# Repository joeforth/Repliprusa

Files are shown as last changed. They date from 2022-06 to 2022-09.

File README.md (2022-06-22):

# Repliprusa
Ongoing project to document modification of Prusa Mini+ 3D printer for Bioprinting. First stage of the process outlined in the conversion guide.
The project uses a modified version of the Feinberg group's Replistruder 4:

https://www.sciencedirect.com/science/article/pii/S2468067220300791

Contact j.forth@ucl.ac.uk if you need any help!

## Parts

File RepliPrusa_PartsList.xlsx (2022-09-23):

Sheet: Replistruder4
Core Parts | Link | Quantity Needed | Purchase Quantity | Detail | Cost
Prusa Mini+ | https://www.prusa3d.com/product/original-prusa-mini-semi-assembled-3d-printer-4/ | 1 | 1 | . | 339 | each
Printhead Conversion | Link | Quantity Needed | Purchase Quantity | Detail | Cost
M8 x 1.25 mm, 150 mm long Fully Threaded Hex Bolt | https://www.ebay.co.uk/itm/383694435663?var=652094637270 | 1 | 3 | . | 1.99 | each
M8 Brass Half Nuts | https://www.ebay.co.uk/itm/383711451484 | 2 | 5 | . | 4.49 | 5 pack
M2 x 20 mm Socket Cap | https://www.ebay.co.uk/itm/321111018634 | 6 | 20 | . | 2.35 | 10 pack
M2 Half Nuts | https://www.ebay.co.uk/itm/383710134373 | 6 | 20 | . | 3.99 | 20 pack
M5 x 130 mm Socket Cap | https://www.amazon.co.uk/Black-Tensile-Socket-screws-Colour/dp/B00SN3221Q | 2 | 5 | . | 3.45 | 5 pack
M5 Nyloc Nuts | https://www.ebay.co.uk/itm/383536842489?var=651919321704 | 2 | 10 | . | 2.99 | 10 pack
60-tooth 8 mm Bore GT2 Pulley | https://www.ebay.co.uk/itm/283138769685 | 1 | 1 | . | 5.75 | each
180 mm, 6 mm Wide GT2 belt | https://www.ebay.co.uk/itm/124146148264?hash=item1ce7afe3a8:g:NI4AAOSwEIBejXSJ | 2 | 2 | . | 3.1 | each
20-tooth, 5 mm Bore GT2 Pulley | https://www.ebay.co.uk/itm/283138769685 | 2 | 1 | . | 2.89 | each
M8 Half Nuts | https://www.ebay.co.uk/itm/383710134373 | 1 | 5 | . | 3.59 | 5 pack
M3 x 10 mm Socket Cap | https://www.ebay.co.uk/itm/383691428657 | ? | 10 | . | 3.99 | 10 pack
M3 Half Nuts | https://www.ebay.co.uk/itm/383710134373 | 5 | 10 | . | 2.79 | 5 pack
Oilite 6 x 10 x 10 mm Bearing | https://www.georgelodgedirect.co.uk/Products/oilite-metric-flanged/AL061010/ | 4 | 4 | . | 10.48 | 4 pack
Oilite 8 x 12 x 8 mm Bearing | https://www.georgelodgedirect.co.uk/Products/oilite-metric-flanged/AL081208/ | 2 | 2 | . | 5.24 | 2 pack
M6 Smooth Rod | https://www.ebay.co.uk/itm/274530374250 | 2 | 2 | 130 mm length needed | 3.54 | 300 mm
M3 x 6 mm Socket Caps | https://www.ebay.co.uk/itm/174196853981?var=473106752313 | ? | 10 | . | 2.29 | 10 pack
M3 x 12 mm Flanged Button Head Screw | https://www.ebay.co.uk/itm/321232365051 | ? | 10 | . | 2.49 | 10 pack
 |  |  |  | Total | 404.41

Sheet: Culture Platform
Culture Bits | Supplier | Code | Quantity | Cost / Item
Insert for GL14 screwcap with tubing outlet, 3.2 mm ID - 1/pk | Fisher Scientific | 4539/06 | 6 | 12.06
GL14 screwcap with tubing outlet - 2 / pk | Fisher Scientific | 4538/02 | 3 pk / 2 | 6.35
GL 45 blue PP screw cap with 3 x GL14 ports - 2/pk | Merck | 4537/04 | 1 | 51.5
Nalgene 50 Platinum cured tubing (OD - ID = 1/8" - 1/16" = 3.2 mm - 1.6 mm) | SLS | 8060-0020 | 1 | 47.98 | Alternative on Amazon - https://www.amazon.co.uk/sourcing-map-Silicone-Flexible-Transfer/dp/B08L33MGJV
Cole-Parmer Polycarbonate Female Luer Fitting Female luer x female luer adapter | Fisher Scientific Ltd | 45501-22 | 1 pk / 25 | 22.73 |  |  | 35 day lead time
Stopcock, Luer Lock to Luer Male, pack of 10 | Merck | S7396-10EA | 1 pack of 10 | 77.4
X25 Male Luer Lock Plug, Nylon | Fisher Scientific Ltd | 45505-56 | 1 pack of 25
Cole-Parmer Polypropylene Male Luer Fitting, Packaging Quantity: 25 Pack | Fisher Scientific | 30800-14 | 1 pk / 25 | 37.41 | 1 |  | 35 day lead time
Intertronics | Supplier | Code | Unit | Unit Cost | Number Required | Total Cost
11 ga - Large gauge stainless steel luer lock dispensing tips – 1 1/2″ long | Intertronics | FIS811150SS1 | EA | 3.9 | 10 | 39
14 ga - Straight blunt end stainless steel dispensing tips – 1″ long | Intertronics | FIS5601095 | 1 pk / 50 | 18 | 1 | 18
15 ga - Straight blunt end stainless steel dispensing tips – 1/2″ long | Intertronics | FIS5601085 | 1 pk / 50 | 16 | 1 | 16
18 ga - Straight blunt end stainless steel dispensing tips – 1/2″ long | Intertronics | FIS5601087 | 1 pk / 50 | 16 | 1 | 16
20 ga - Straight blunt end stainless steel dispensing tips – 1/2″ long | Intertronics | FIS5601088 | 1 pk / 50 | 16 | 1 | 16
23 ga - Straight blunt end stainless steel dispensing tips – 1/2″ long | Intertronics | FIS5601091 | 1 pk / 50 | 16 | 1 | 16
18 ga - 0.5" Flexible Dispensing Tips - 0.5" long | Intertronics | FIS5601287 | 1 pk / 50 | 41.05 | 1 | 41.05
20 ga - 0.5" Flexible Dispensing Tips - 0.5" long | Intertronics | FIS5601288 | 1 pk / 50 | 41.05 | 1 | 41.05
22 ga - 0.5" Flexible Dispensing Tips - 0.5" long | Intertronics | FIS5601289 | 1 pk / 50 | 41.05 | 1 | 41.05
Cutting
TCT SCRIBER & GLASS CUTTER 150MM | Onecall | 633657 | 1 | 2.52
SELF HEALING CUTTING MAT A3 | Onecall | TL16887 | 1 | 5.69
Metal Safety Rule | https://www.amazon.co.uk/Guard-Centimetres-Quilting-Imperial-Global-Ltd/dp/B01HI8U6TQ |  |  |  | 1
Alternative Connectors
4 mm Barbed Connectors (2-3 mm ID tubing) | pihut
Luer-to-Tubing Connector | Merck | Z118028-4EA | 1 pk / 4 | 31 | 2 | 62
Connector Barbed 1/16 x 1/16 | Thames Restek | P-801 | 1 | 0.54 | 20 | 10.8

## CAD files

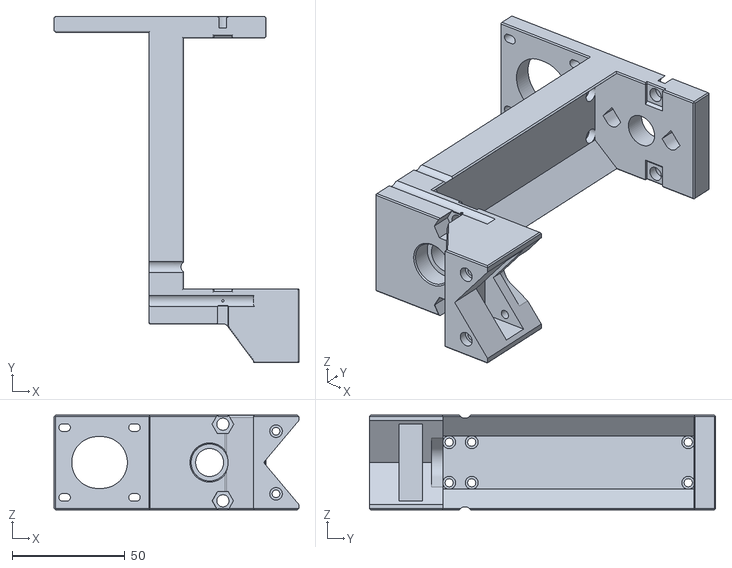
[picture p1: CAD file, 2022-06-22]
stls/Replistruder4_Core.stl
108.6 x 153.6 x 42.0

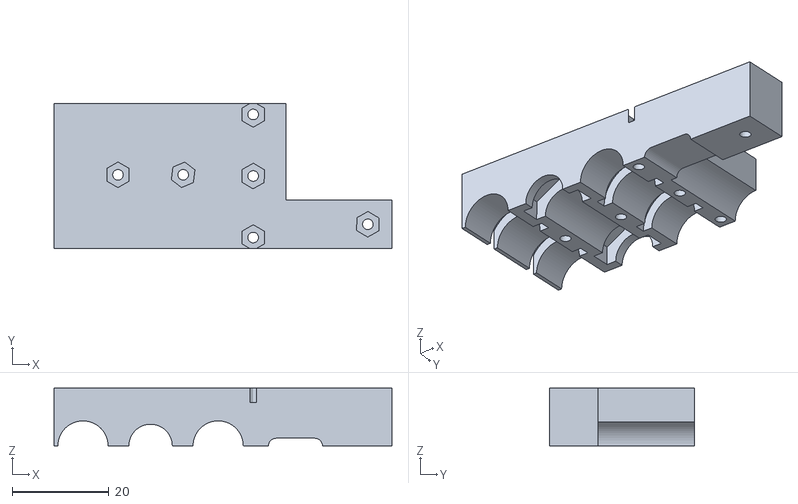
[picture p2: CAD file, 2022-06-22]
stls/ModCarriage_Version2_NutSide v5.stl
70.0 x 30.0 x 12.0

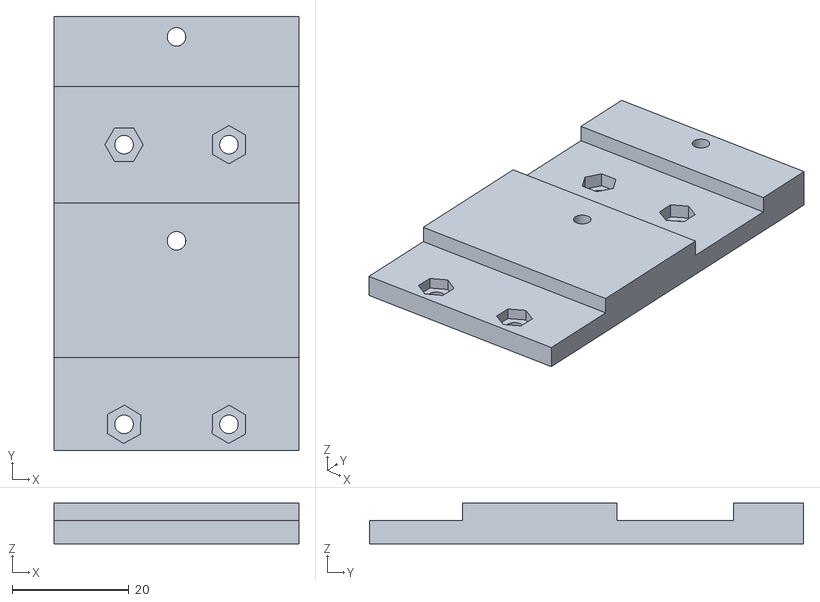
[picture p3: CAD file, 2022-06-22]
stls/Mount_v2 v3.stl
42.0 x 74.5 x 7.00

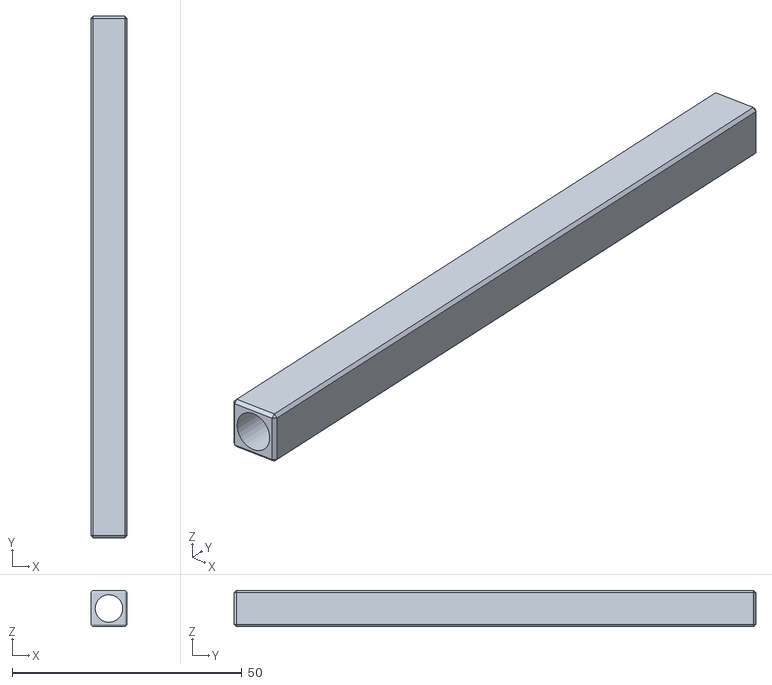
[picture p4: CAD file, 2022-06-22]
stls/Replistruder4_CoreSupport_Modified v2.stl
7.90 x 113.5 x 7.90

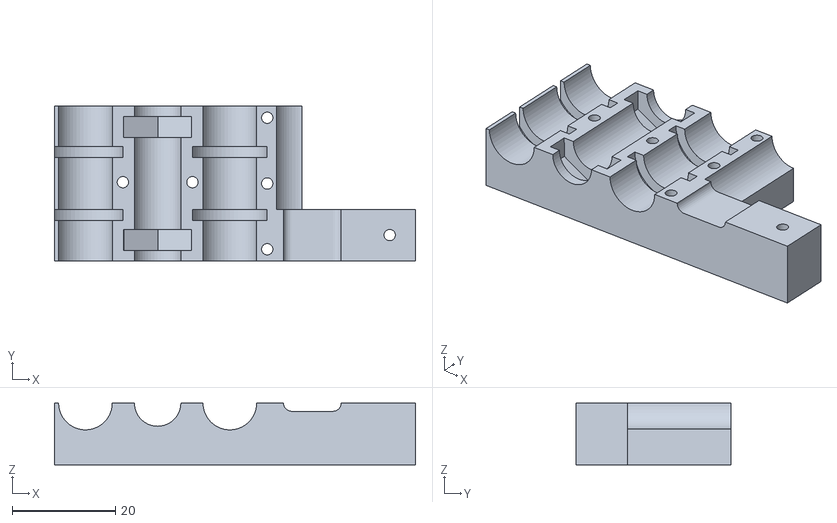
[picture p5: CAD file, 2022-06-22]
stls/ModCarriage_Version2_ScrewSide v5.stl
70.0 x 30.0 x 12.0

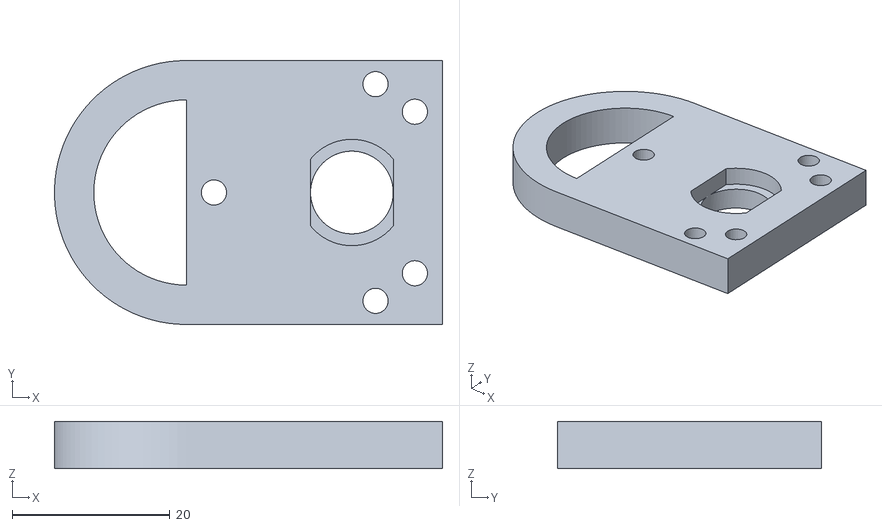
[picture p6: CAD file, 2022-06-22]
stls/Bottom_Plate_shiftedbolts_v2 v0.stl
49.2 x 33.5 x 6.00

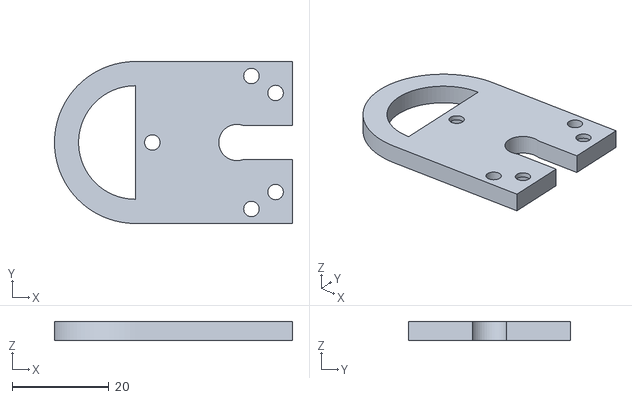
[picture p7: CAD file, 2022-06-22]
stls/Top_Plate_shifterbolts_v2 v2.stl
49.2 x 33.5 x 4.00

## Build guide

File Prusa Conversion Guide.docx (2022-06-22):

Prusa Conversion Guide, v0.1

Parts to Print

Settings: 50% infill, 0.16 mm Creality, 0.15 mm Mini+, 0.15 mm Ultimaker

Replistruder4_Core.stl – 16:30 / 12:27 / 9:15

Mount_v2 v3.stl – 1:40 / 1:47 / 2:00

2x Replistruder4_CoreSupport_Modified v2.stl – 1:35 / 1:10 / 1:21

Top_Plate_shifterbolts_v2 v2.stl – 0:44 / 0:36 / 0:34

Bottom_Plate_shiftedbolts_v2 v0.stl – 1:00 / 0:56 / 0:44

Version2_NutSide v5.stl – 2:37 / 1:33 / 1:33

Version2_ScrewSide v5 – 2:30 / 1:33 / 1:32

Mini+_allparts_nocore.gcode – 8:44

UM2_Replistruder4_Core – 9:13

Firmware Modification:

Download: Prusa-Firmware-Buddy-master

Modify: ./include/marlin/Configuration_MINI_adv.h

Change line 988 to:

#define Z_MIN_POS -80

Change lines 493 and 494:

#define PREVENT_COLD_EXTRUSION

#define EXTRUDE_MINTEMP 0

Run:

python3 ./utils/build.py --generate-bbf

Note that you will have permission errors if you copy files compiled on one computer to run them on another

Now copy:

/build/products/mini_release_boot.bbf

To a USB drive

This should be read automatically (you don't need to hit any buttons) - there will be a warning about how the key for the firmware is invalid (hit ignore).

Converting Your Prusa Mini+ to a Liquid/Gel FrankenPrinter

Part 1 – Gutting your Beloved Printer

You’ll need:

Pliers

2.5 mm Allen / Hex Wrench

Small flathead screwdriver

Steps

1. Unload any filament already loaded in the printer, then switch off and wait for everything to cool down.
2. Unscrew the large brass bolt from the extruder mount and remove the plastic tube that usually carries the filament.

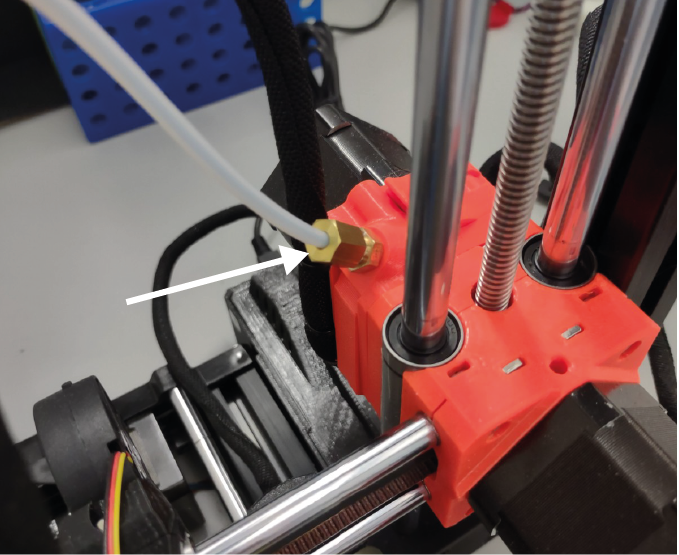
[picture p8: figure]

3. Open up the electronics enclosure and remove plugs 1-5, leaving the black/blue/red/green extruder stepper motor plugged in.

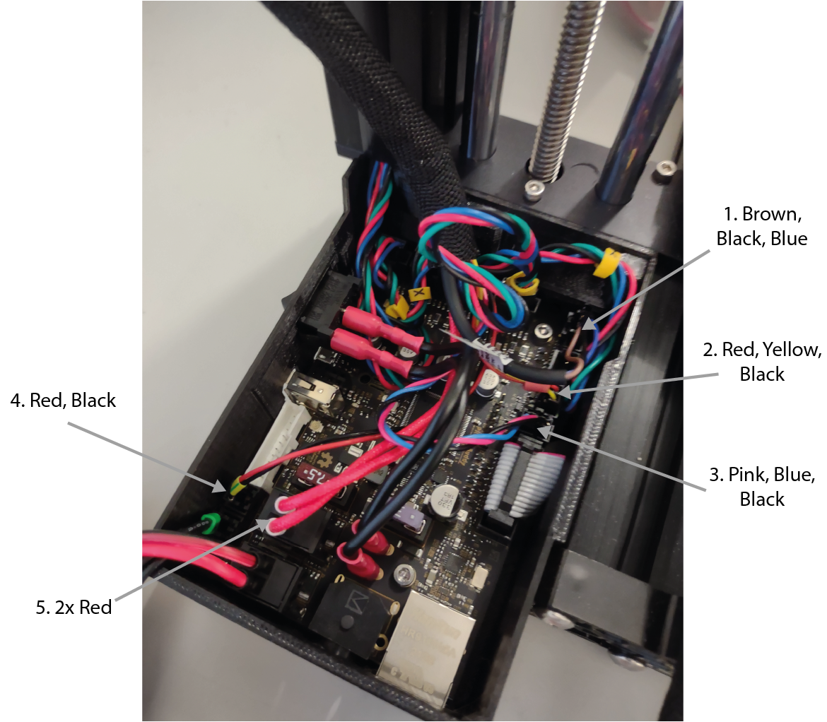
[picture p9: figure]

4. While you’re here – it’s time for the scary part of the operation. You need to physically break a connection on the motherboard to be able to install custom firmware. Take a small, flathead screwdriver and break the part of the logic board shown in the photo below. Apply a reasonable amount of force to the thinnest bit of the board – you should end up with something that looks like this:

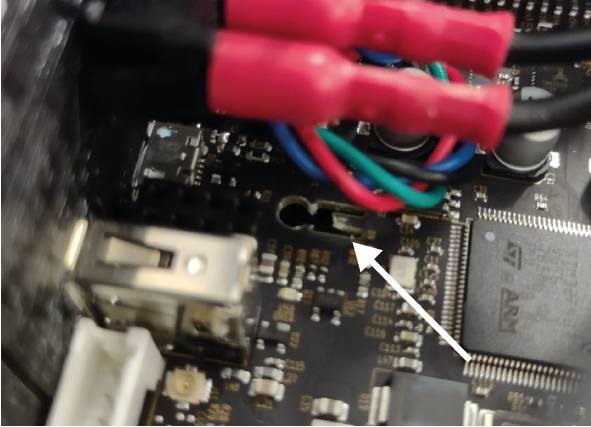
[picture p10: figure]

Before doing this, you may want to consult an emotional support website – either a more practical one:

https://help.prusa3d.com/article/flashing-custom-firmware-mini_14

Or simply some pictures of puppies.

5. Cut the 3 cable ties attached to the extruder stepper mount and remove the wires from the protective sheath, and gently remove the protective sheath.

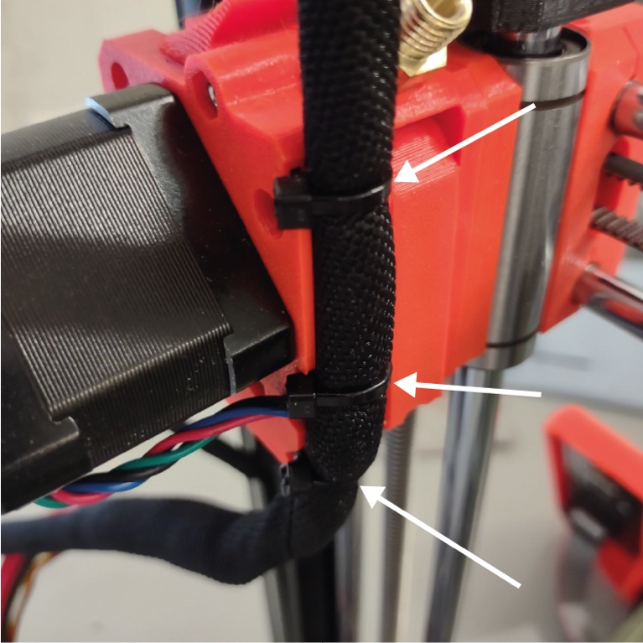
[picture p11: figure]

6. Place the cable from the stepper motor back in the protective sheath and replace the motherboard cover and the screws that hold it in place. You should have something that looks like this:

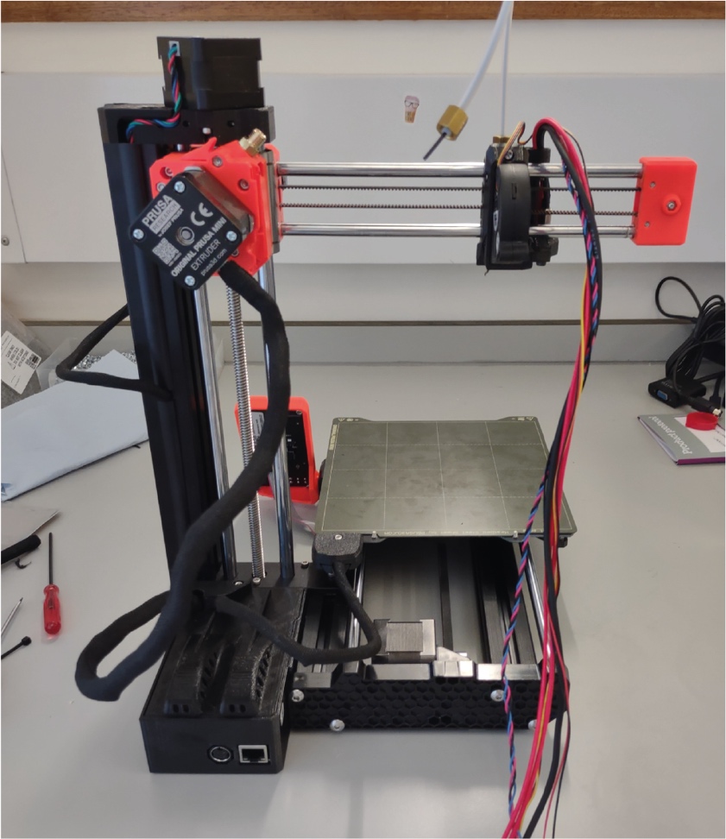
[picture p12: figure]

7. Now it’s time to remove the hot-end. Remove the screws shown by the white below (it is almost certainly possible to achieve this while removing fewer screws).

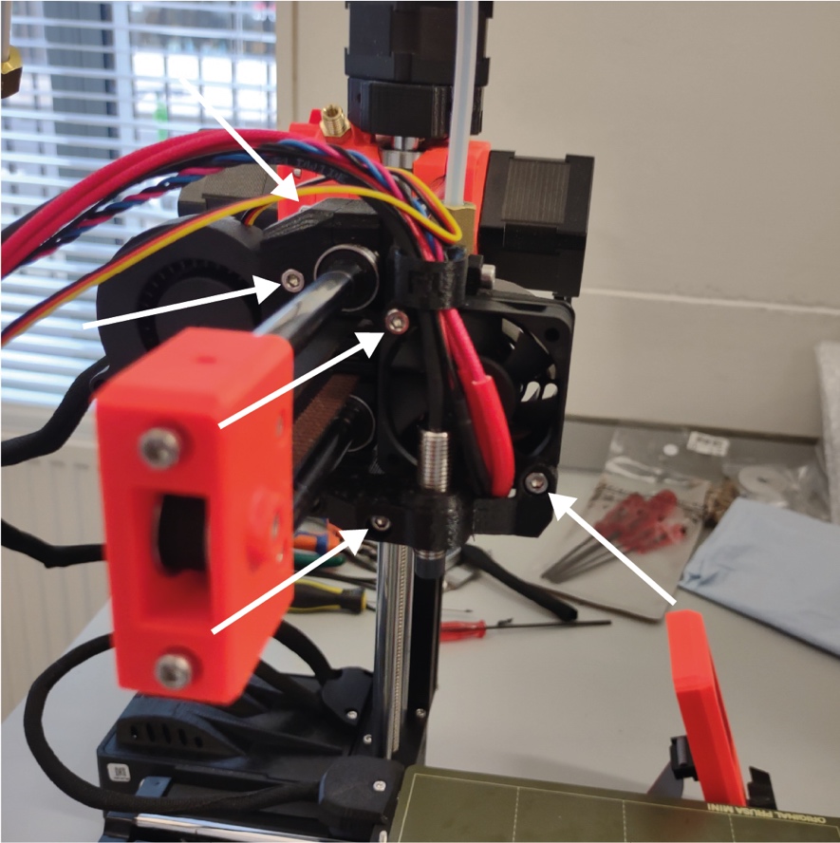
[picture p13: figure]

8. Finally, (1.) pull the fan out – this might take a bit of force and (2.) remove the final screw attaching the hot end.

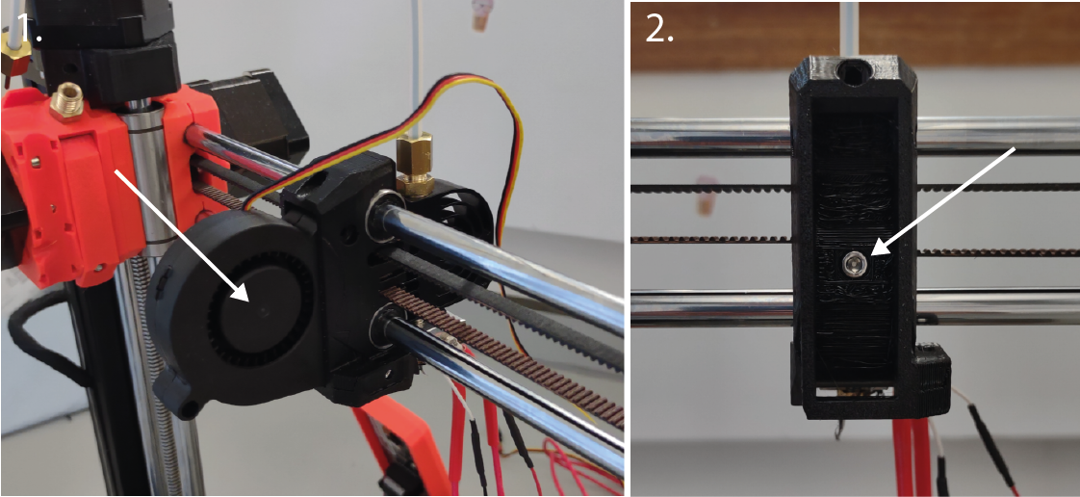
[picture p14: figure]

9. You should be left with something that looks like the photo below – well done! You’re ready to assemble and mount your new printhead!

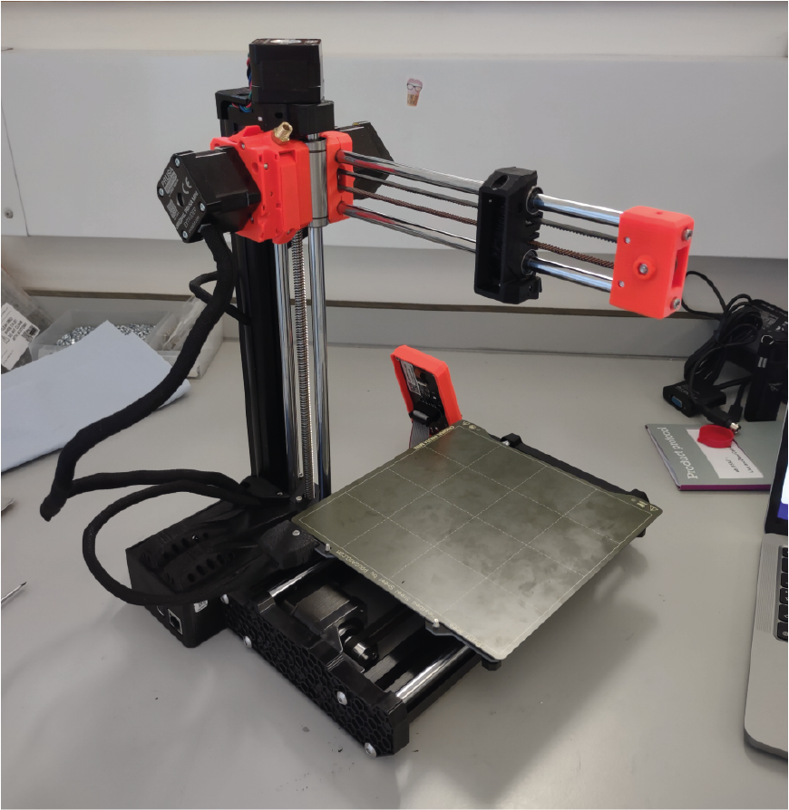
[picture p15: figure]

Part 2 – Assembling Your Forklistruder_Mod Printhead
